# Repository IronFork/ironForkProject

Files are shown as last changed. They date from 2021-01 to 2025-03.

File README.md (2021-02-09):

# ironForkProject
 robotic arm helping people with disabilities to eat
 
 https://ironfork.fr

READ ME

I - INTRODUCTION

  a) Présentation
  
  b) Objectifs du projet
  
II - MONTER LE ROBOT

  a) Imprimer les pièces en 3D
  
  b) Se procurer les moteurs
  
  c) Se procurer les composants annexes 
  
III - FAIRE FONCTIONNER LE ROBOT

IV - EXPLICATION DU CODE SOURCE

  a) La partie mécanique 
  
  b) La partie programmation
  
V - PISTES D'AMÉLIORATION

I - INTRODUCTION 

a) Présentation : 
Projet mené par un groupe de 12 étudiants en partenariat avec l'IEM "Christian Dabbadie" dans le cadre de leurs études à Centrale Lille. 

b) Objectifs du projet : 
Concevoir un bras robotique permettant aux personnes en situation de handicap d'avoir une plus grande autonomie lors de leurs repas. 
Projet en open source avec une licence GPL. 
L'un des objectifs du projet est de rendre le bras imprimable en 3D facilement dans un fablab.

I - MONTER LE ROBOT 

Vous aurez besoin d'une imprimante 3D et de ... bobines de PLA. Le reste des composants à commander est indiqué dans les étapes suivantes. Le budget estimé est de 500€ environs. 

a) Imprimer les pièces en 3D : 
Ouvrir le dossier fichiers_stl. Ce dossier contient les fichiers STL de chaque pièce du robot, organisées en sous-ensembles. Un sous-dossier nommé "assemblages" contient les fichiers STL des différents sous-ensembles, et de l'assemblage complet. 

Liste des pièces à imprimer en 3D : 

Pour le socle : 
  - 3 sous-socles différents (c'est le plancher du robot, les 3 sous-socles sont sur le même ficher STL)
  - 1 bol
  - 1 socle (en forme de petite tablette)
  - 1 adaptateur socle-moteur (permet de fixer le moteur sous le socle)
  - 1 poulie socle (poulie fixée sur l'axe moteur)
  
Pour la Tourelle : 
  - 1 Tourelle (placée en liaison pivot avec le socle, elle soutient le bras)
  - 1 poulie tourelle ( poulie fixée dans l'axe de la tourelle et reliée à la poulie socle par une courroie)
  - 2 adaptateurs tourelle-moteurs (permettent de fixer 2 moteurs sur la tourelle)
  
Pour le bras : 
  - 1 bras Tourelle (c'est le bras relié à la tourelle en pivot)
  - 1 adaptateur bras-moteur (permet de fixer le moteur sur le bras)
  
Pour l'avant-bras : 
  - 1 avant-bras (ressemble au bras-tourelle mais est légèrement différent)
  - 1 adaptateur avant-bras-moteur (permet de fixer le moteur)
  
Pour la pince : 
  - 1 pince 

Pour l'assemblage, référez-vous aux fichiers STL représentant les sous-ensembles du robot. 

b) Se procurer les moteurs : 
Vous aurez besoin de cinq moteurs dynamixel XL430-W250-T.
documentation technique sur github : https://github.com/ROBOTIS-GIT/emanual/blob/master/docs/en/dxl/x/xl430-w250.md

c) Se procurer les composants annexes : 
voir notice. (visserie, fils électriques, rasberry pi, carte de programmation, etc... )

d) Assembler le robot : 
Vous devez vous référer au dossier fichiers_stl pour voir le rôle de chaque composant au sein de l'assemblage complet. 
Référez-vous également au schéma électrique pour les différents branchements. 
Référez-vous à la notice pour vous aider

L'assemblage du robot est maintenant terminé. 

II - FAIRE FONCTIONNER LE ROBOT  

Version 1 du robot 

La trajectoire est programmée par l'ensemble des fichiers matlab 
puis est lue par le programme IronFork.c

Version 2 du robot 

Compiler IronForkV3.c et l'executer. Le robot pourra apprendre sa trajectoire pendant une phase de teaching et ensuite la répeter. 

III - EXPLICATION DU CODE SOURCE 

a) La partie mécanique

Le schéma cinématique : 
Nous avons choisi un nombre de 5 pièces d'un point de vue cinématique. Elles sont reliées en série au bâti par cinq liaisons pivot. Une pivot verticale lie le BATI avec la TOURELLE, une pivot horizontale lie la TOURELLE au BRAS, une pivot horizontale lie le BRAS à l'AVANT-BRAS, et une liaison pivot horizontale lie l'AVANT-BRAS à la PINCE. 
Ce choix de 4 pièces et de cinq liaisons pivot nous permet de positionner la PINCE à n'importe quel endroit dans l'espace, et de réaliser un maximum de mouvements en gardant la PINCE à l'horizontal (ce qui permet de déplacer une cuillère sans renverser son contenu). Ce choix de cinématique permet des mouvements fluides et précis. Référez-vous au fichier STL de l'assemblage complet pour vous représenter l'architecture du robot. 

La tourelle : 
La tourelle est au bâti par une liason pivot verticale. Cette liaison permet au robot de tourner sur lui même et de déplacer la cuillère de manière grossière latéralement de gauche à droite. 
Cette liasion qui est la première est la seule à supporter toute la structure du robot, et subit donc beaucoup d'efforts. Il y a également beaucoup de forttements, de par l'appui de la tourelle sur le bâti. Nous avons choisi d'utiliser un coussinet à collerette entre le bati et la tourelle pour minimiser les frottements. La liasion est motorisée par un servomoteur Dynamixel positionné à quelques centimètres de la liaison, et relié par une liaison poulie-couroie. Cela permet de résoudre le problème de coaxialité du moteur avec la liasion, et d'écentuels efforts supportés par l'axe du moteur.

La tourelle et le bras : 
La tourelle et le bras sont reliés par une liaison pivot horizontale. Cette liaison contribue grandement au mouvement d'avant en arrière de la cuillère. 
Encore une fois, cette liasion supporte une bonne partie de la structure du robot, surtout quand celui-ci est étendu. Dans ce cas là, le couple dans l'axe de la liaison est particulièrement élevé. C'est pourquoi nous avons choisi de placer non pas un, mais deux servomoteurs Dynamixel en parallèle de manière à pouvoir axionner cette liasion avec une puissance suffisante. Deux adaptateurs sont vissés au bâti avec des vis à bois permettent de fixer les servomoteurs. 

Le bras et l'avant-bras : 
Le bras est relié à l'avant-bras par une liasion pivot motorisée par un servomoteur Dynamixel. Cette laison contribue grandement au mouvement vertical de bas en haut de la cuillère. Un adaptateur vissé au bras par des vis à bois permet de fixer le moteur. 

L'avant-bras et la pince : 
L'avant-bras et la pince sont reliés entre eux par une liaison pivot motorisée par un servomoteur Dynamixel. Cette liaison permet d'effectuer un mouvement vertical de précison, à la manière d'un poignet. Un adaptateur vissé à l'avant-bras permet de fixer le moteur. 

La pince : 
La pince présente une fente ainsi qu'un trou. Ce trou permet d'y placer un insert de filletage, et la fente permet d'y glisser un manche de cuillère. Ainsi, avec une vis de pression, la cuillère peut être bloquée dans la fente. L'avantage de ce système est qu'il permet l'utilisation d'une cuillère quelconque. 

Le bol : 
Un bol imprimé en 3D est fixé sur le support. ce bol a une forme particulière qui permet à la nourriture d'être centrée dans la zone de pelletage. De plus, le rebord avancé peu haut et le rebord éloigné élevé permettent une introduction de la cuillère aisée, et un raclage facilité. L'avantage de ce système est qu'il permet de n'avoir qu'un seul et unique geste de peletage pour le robot. L'inconvénient est le côté sanitaire : il faut imprimer le bol en PET, et les stries de l'impression 3D peuvent occasionner des copeaux de plastiques dans la nourriture lors du raclage. 

b) La partie programmation

cf commentaires

IV - PISTES D'AMELIORATION

- sécurité, détection d'erreur informatique
- tests en conditions réeelles (personne en situation de handicap)
- améliorer le système de fixation de la cuillère 
- réduire le volume
- trouver des composants moins cher
- reconnaissance faciale
- ...

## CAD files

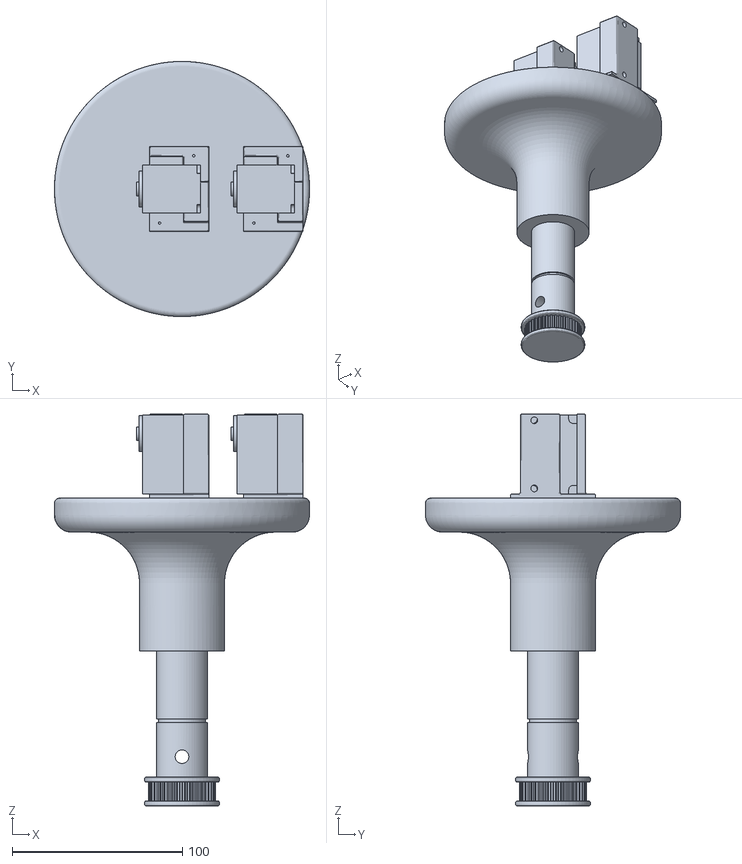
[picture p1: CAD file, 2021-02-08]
Ancien projet/fichiers_STL/assemblages/Tourelle.stl
150.0 x 150.0 x 230.4

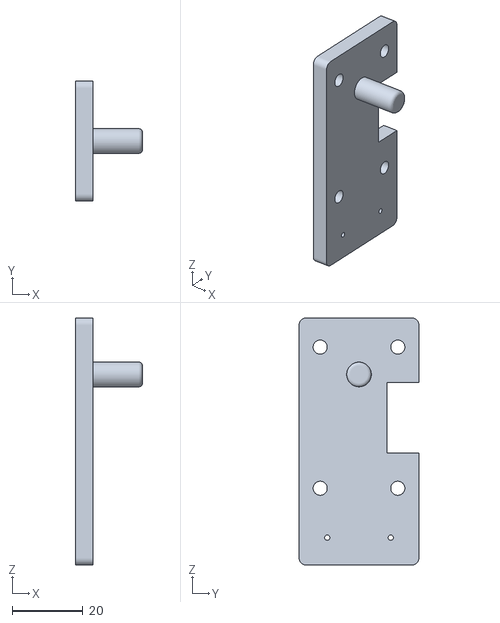
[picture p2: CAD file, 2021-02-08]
Ancien projet/fichiers_STL/avant-bras/Adaptateur Bras-Moteur.stl
19.0 x 34.0 x 70.0

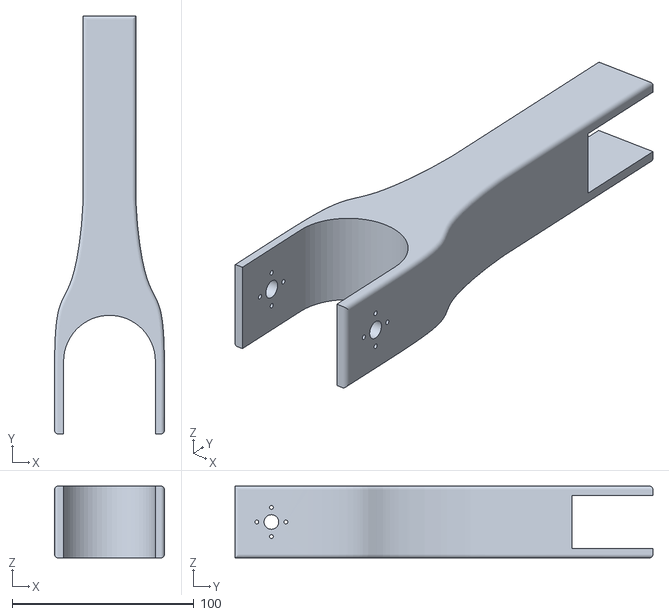
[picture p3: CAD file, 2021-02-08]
Ancien projet/fichiers_STL/bras/Bras Tourelle.stl
60.5 x 229.7 x 39.5

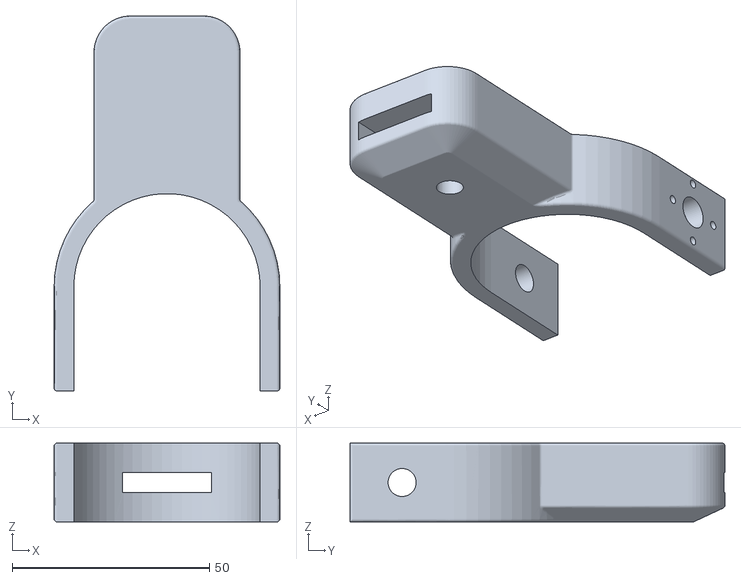
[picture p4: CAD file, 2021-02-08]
Ancien projet/fichiers_STL/pince/Pince-2.stl
57.2 x 95.0 x 20.0

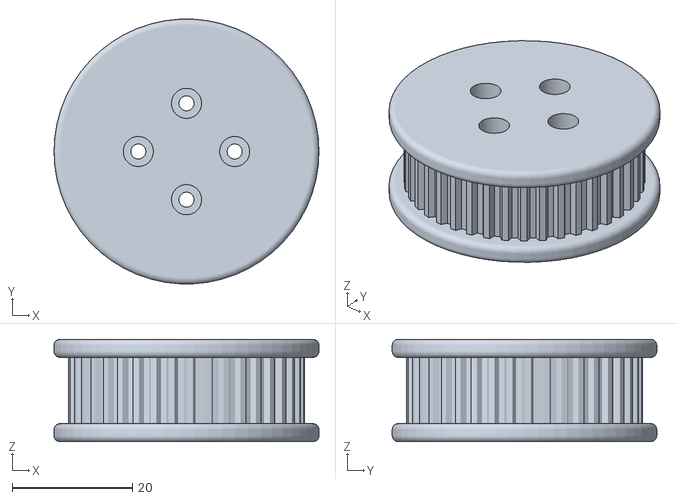
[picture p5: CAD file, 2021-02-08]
Ancien projet/fichiers_STL/socle/Poulie Socle.stl
44.0 x 43.9 x 17.0

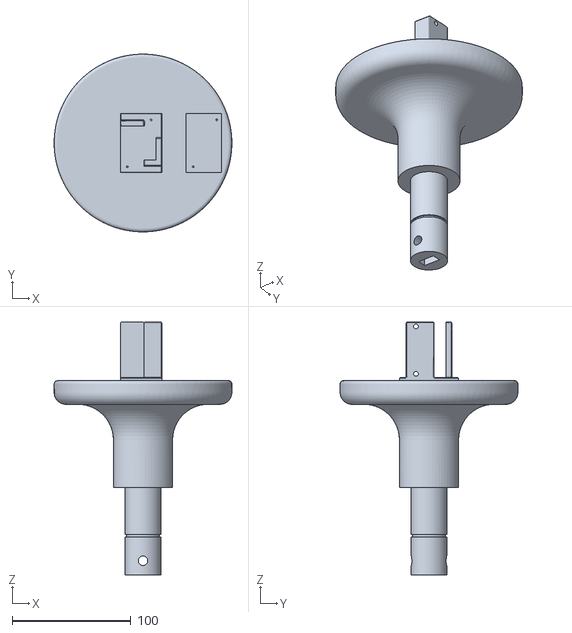
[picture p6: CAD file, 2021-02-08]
Ancien projet/fichiers_STL/tourelle/Tourelle.stl
150.0 x 150.0 x 213.4

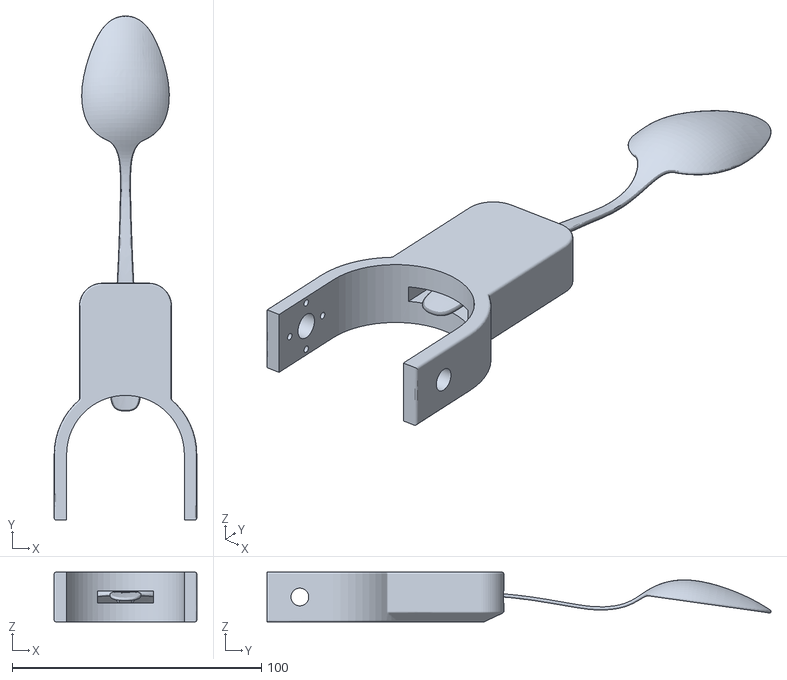
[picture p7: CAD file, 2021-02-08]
Ancien projet/fichiers_STL/assemblages/Pince-2.stl
57.2 x 202.2 x 20.0

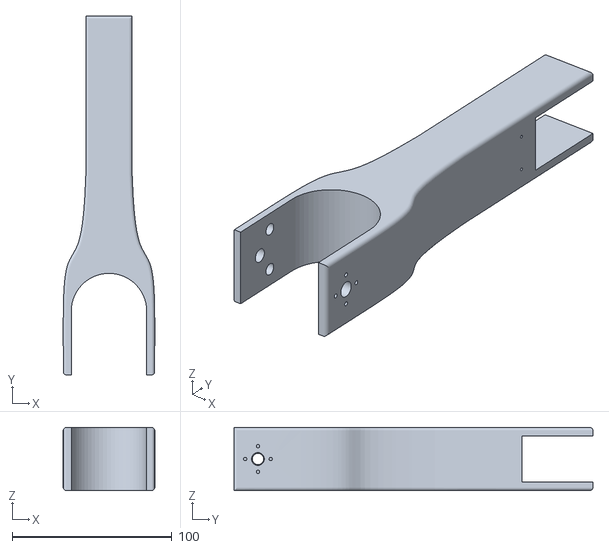
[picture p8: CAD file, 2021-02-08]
Ancien projet/fichiers_STL/avant-bras/Avant-Bras.stl
57.3 x 224.7 x 39.5

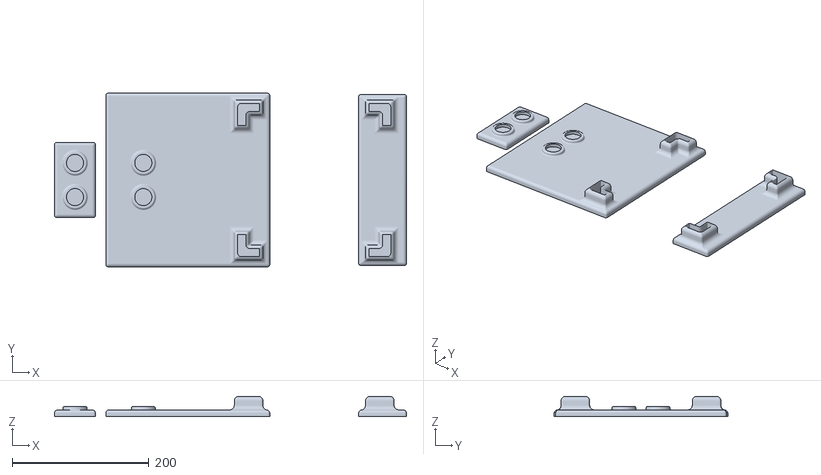
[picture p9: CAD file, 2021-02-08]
Ancien projet/fichiers_STL/socle/Sous-Socles.stl
515.0 x 254.0 x 30.0

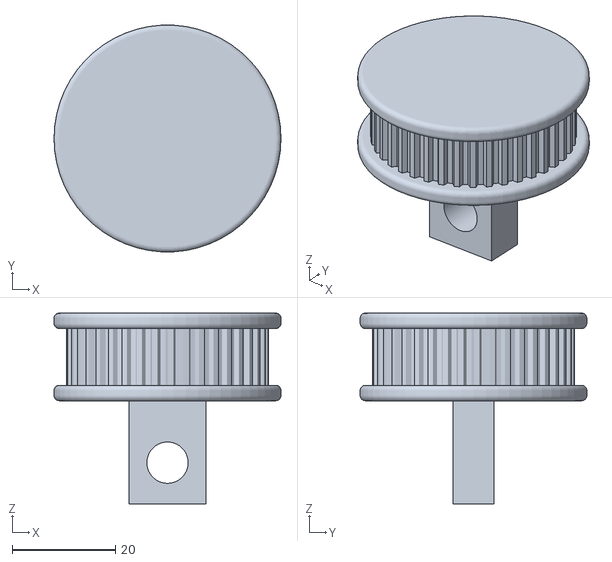
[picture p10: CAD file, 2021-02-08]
Ancien projet/fichiers_STL/tourelle/Poulie Tourelle.stl
44.0 x 43.9 x 37.0

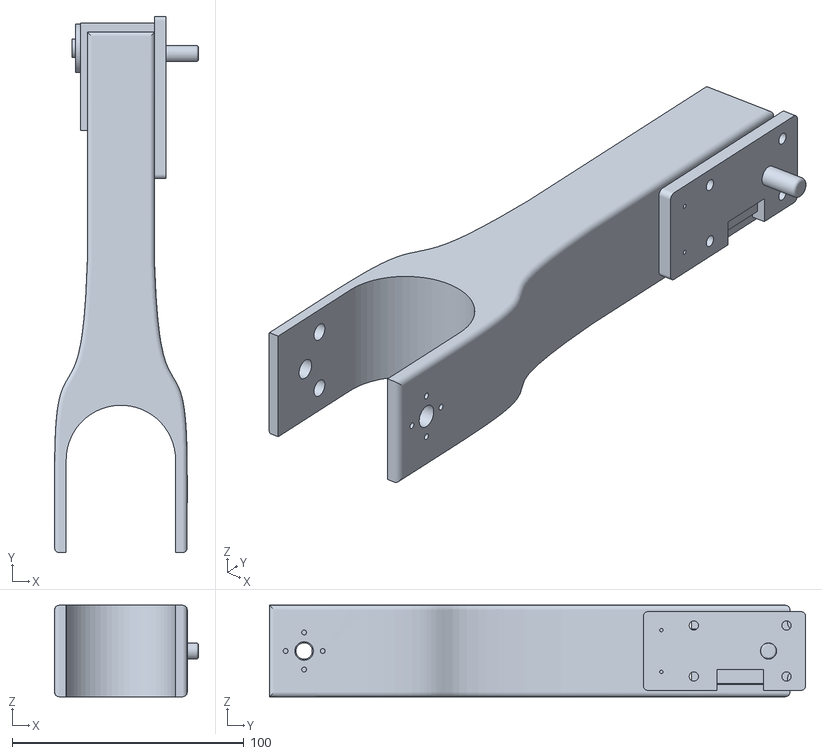
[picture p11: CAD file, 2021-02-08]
Ancien projet/fichiers_STL/assemblages/Avant-Bras.stl
62.2 x 231.4 x 39.5

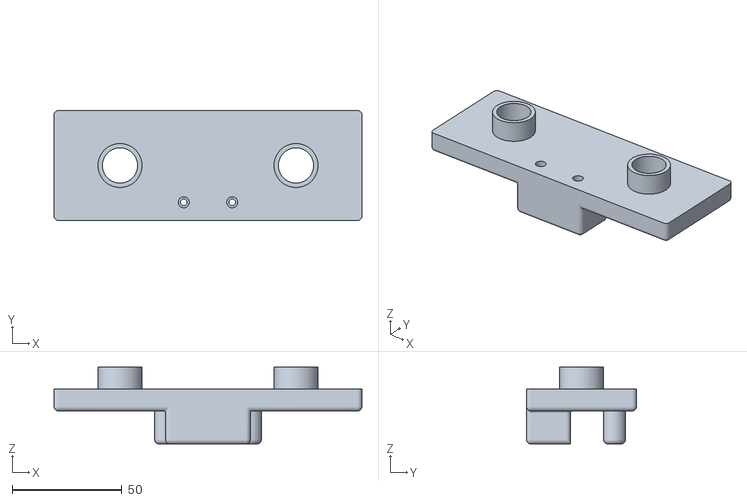
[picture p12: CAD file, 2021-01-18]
Ancien projet/fichiers_STL/socle/Adaptateur Socle-Moteur-1.stl
140.0 x 50.0 x 35.0

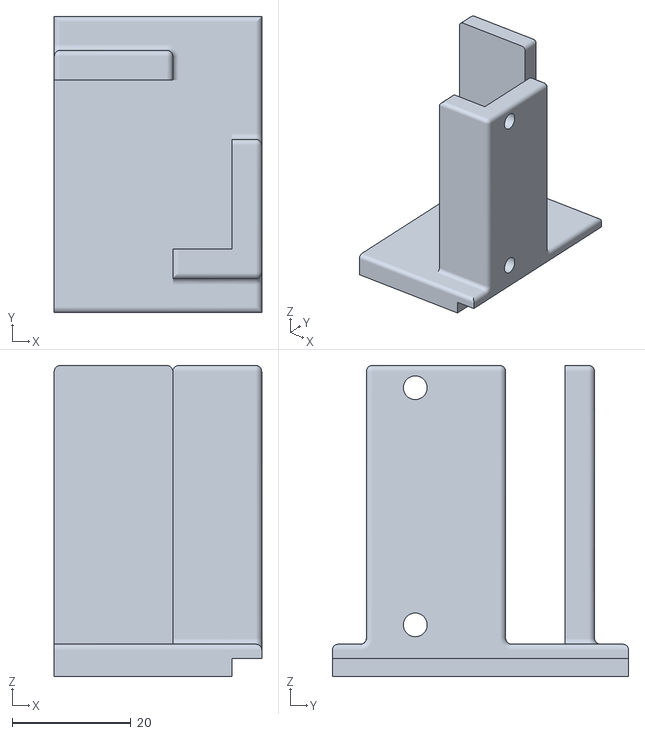
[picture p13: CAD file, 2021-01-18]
Ancien projet/fichiers_STL/tourelle/Adaptateur Tourelle Moteur (1).stl
35.0 x 50.0 x 52.4

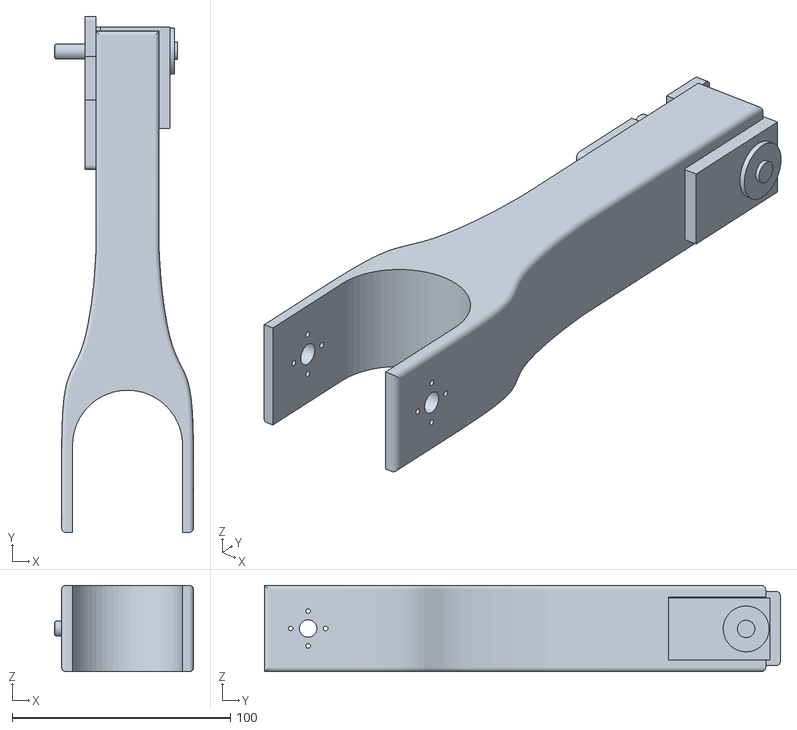
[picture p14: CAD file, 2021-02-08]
Ancien projet/fichiers_STL/assemblages/Bras.stl
63.8 x 236.4 x 39.5

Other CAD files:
Ancien projet/fichiers_STL/socle/Socle.stl
Ancien projet/fichiers_STL/socle/Bol.stl

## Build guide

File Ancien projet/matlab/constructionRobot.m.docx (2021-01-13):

%% création du robot

IronFork = rigidBodyTree;

% création des parties du robot

tourelle = rigidBody('tourelle');

bras = rigidBody('bras');

avantBras = rigidBody('avantBras');

pince = rigidBody('pince');

% création des joint entre parties

jnt1 = rigidBodyJoint('jnt1','revolute');

jnt2 = rigidBodyJoint('jnt2','revolute');

jnt3 = rigidBodyJoint('jnt3','revolute');

jnt4 = rigidBodyJoint('jnt4','revolute');

%% Paramètrage des joints

% Liaison bati-tourelle

jnt1.HomePosition = alpha1; %position initiale du moteur

%Placement de la liaison.

tform1 = trvec2tform([0, 0, 0]);

setFixedTransform(jnt1,tform1); %applique la transformation

tourelle.Joint = jnt1; %liaison du joint au corps

% Liaison tourelle-bras

jnt2.HomePosition = alpha2; %position initiale du moteur

tform2 = trvec2tform([0, 0, AB])*eul2tform([0, -pi/2, 0]);

setFixedTransform(jnt2,tform2);

bras.Joint = jnt2;

% Liaison bras-avantBras

jnt3.HomePosition = alpha3; %position initiale du moteur

tform3 = trvec2tform([BC, 0, 0]);

setFixedTransform(jnt3,tform3);

avantBras.Joint = jnt3;

% Liaison avantBras-pince

jnt4.HomePosition = alpha4; %position initiale du moteur

tform4 = trvec2tform([CD, 0, 0]);

setFixedTransform(jnt4,tform4);

pince.Joint = jnt4;

%% Mise en place robot

addBody(IronFork,tourelle,'base');

addBody(IronFork,bras,'tourelle');

addBody(IronFork,avantBras,'bras');

addBody(IronFork,pince,'avantBras');

%% Ajout end effector

cuillereBout = rigidBody('cuillereBout');

tform5 = trvec2tform([DE, 0, 0])*eul2tform([0, 0, pi/2]); % User defined

setFixedTransform(cuillereBout.Joint,tform5);

addBody(IronFork,cuillereBout,'pince');

%% Visualisation

q0=homeConfiguration(IronFork);

showdetails(IronFork);

show(IronFork,q0);

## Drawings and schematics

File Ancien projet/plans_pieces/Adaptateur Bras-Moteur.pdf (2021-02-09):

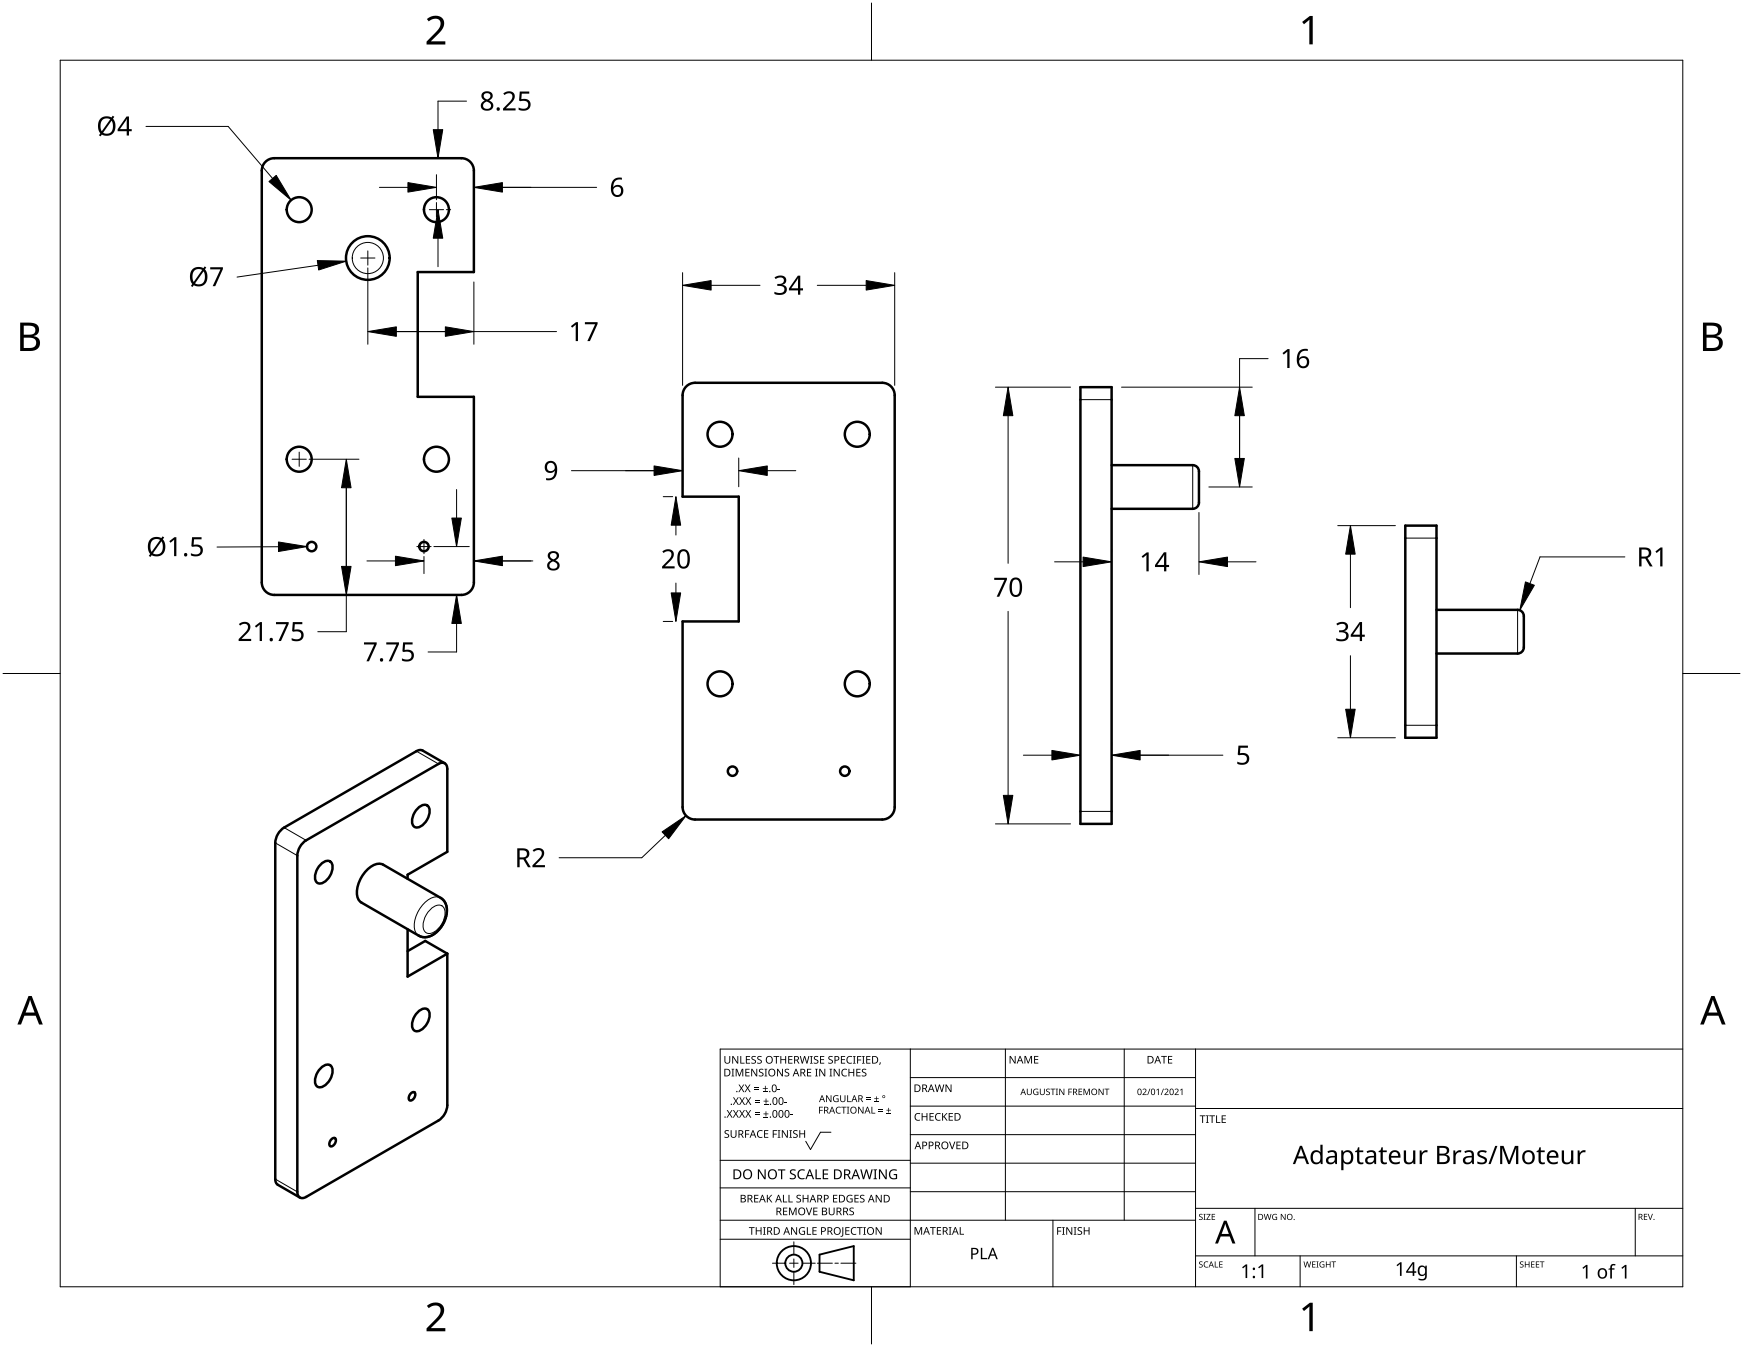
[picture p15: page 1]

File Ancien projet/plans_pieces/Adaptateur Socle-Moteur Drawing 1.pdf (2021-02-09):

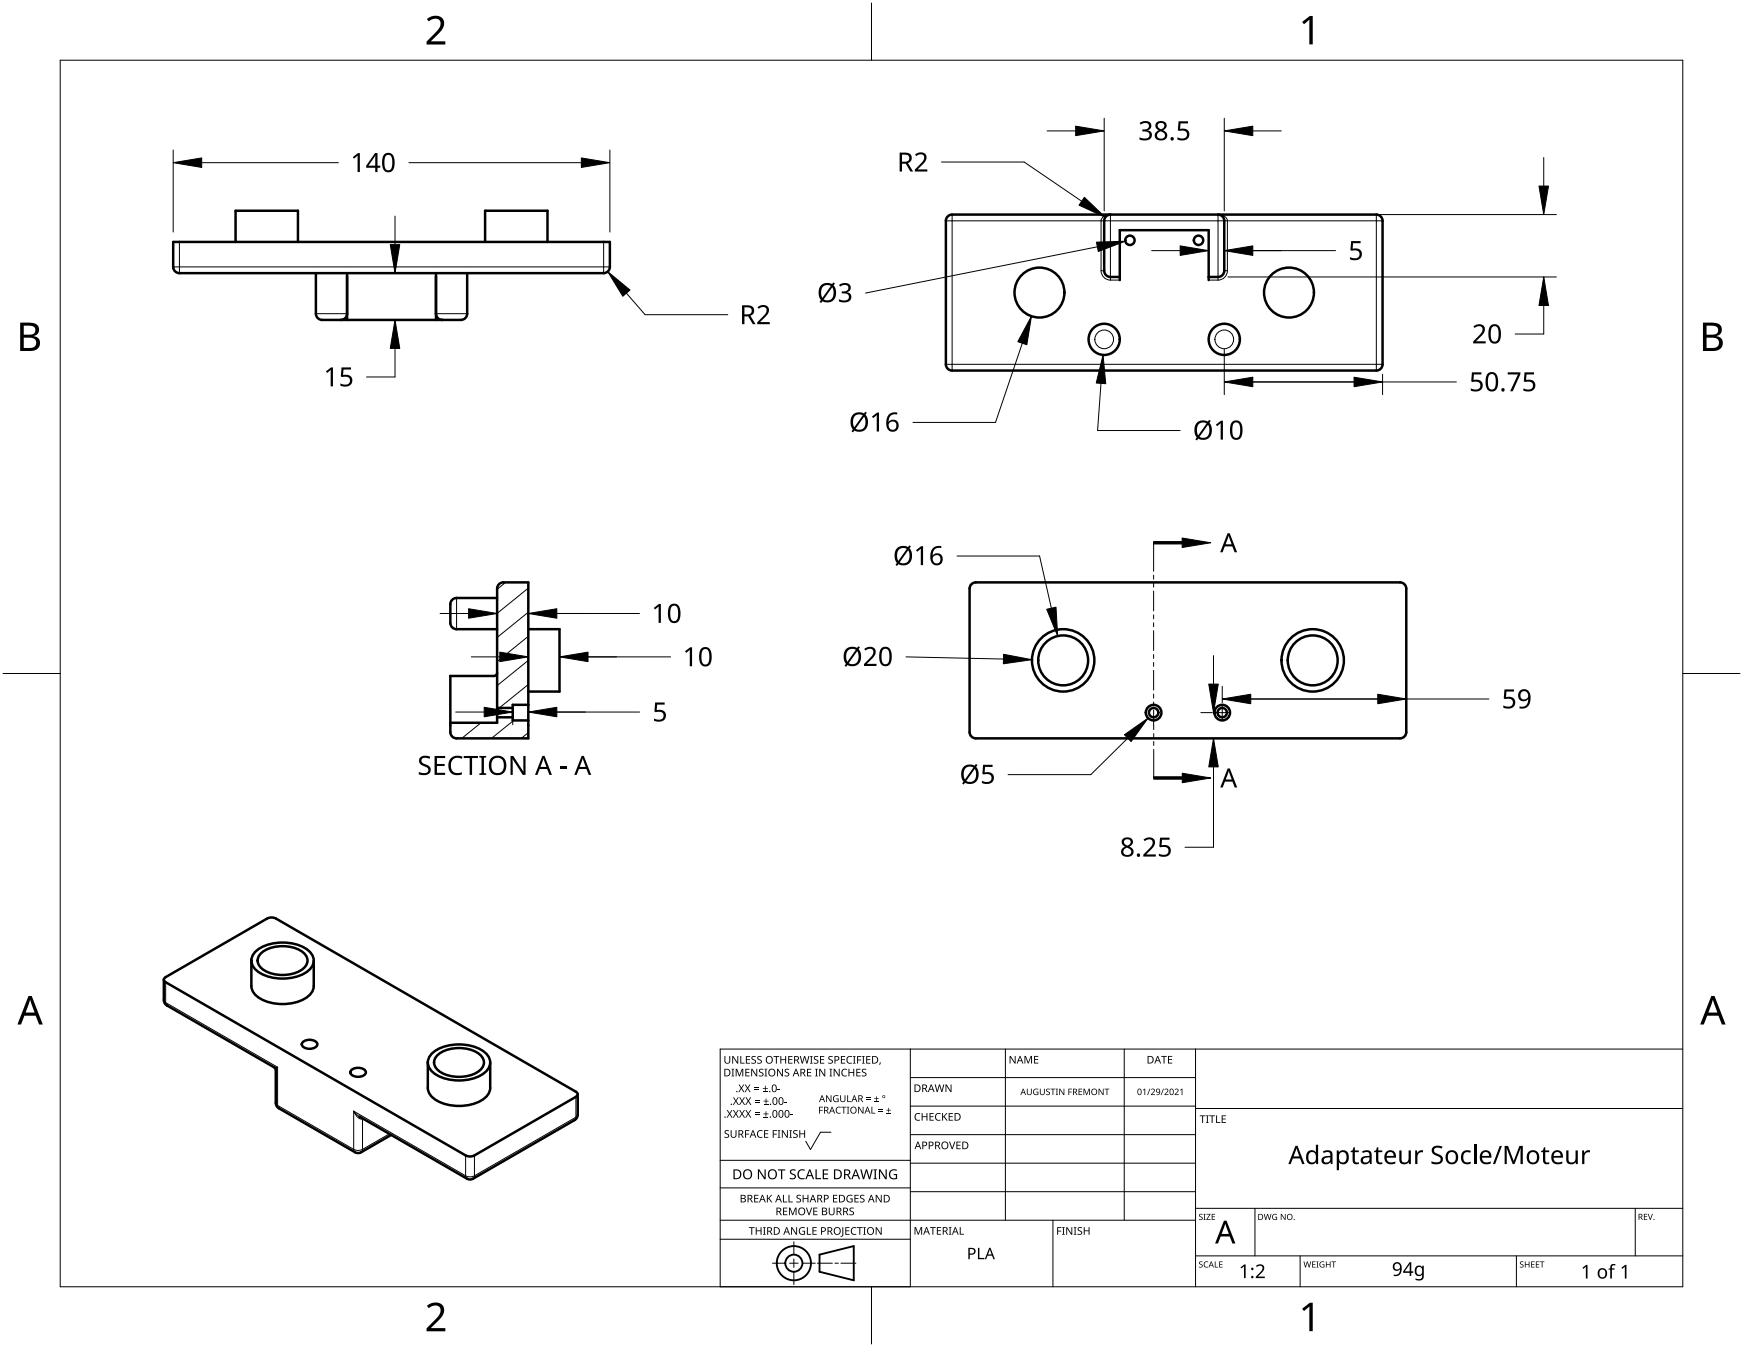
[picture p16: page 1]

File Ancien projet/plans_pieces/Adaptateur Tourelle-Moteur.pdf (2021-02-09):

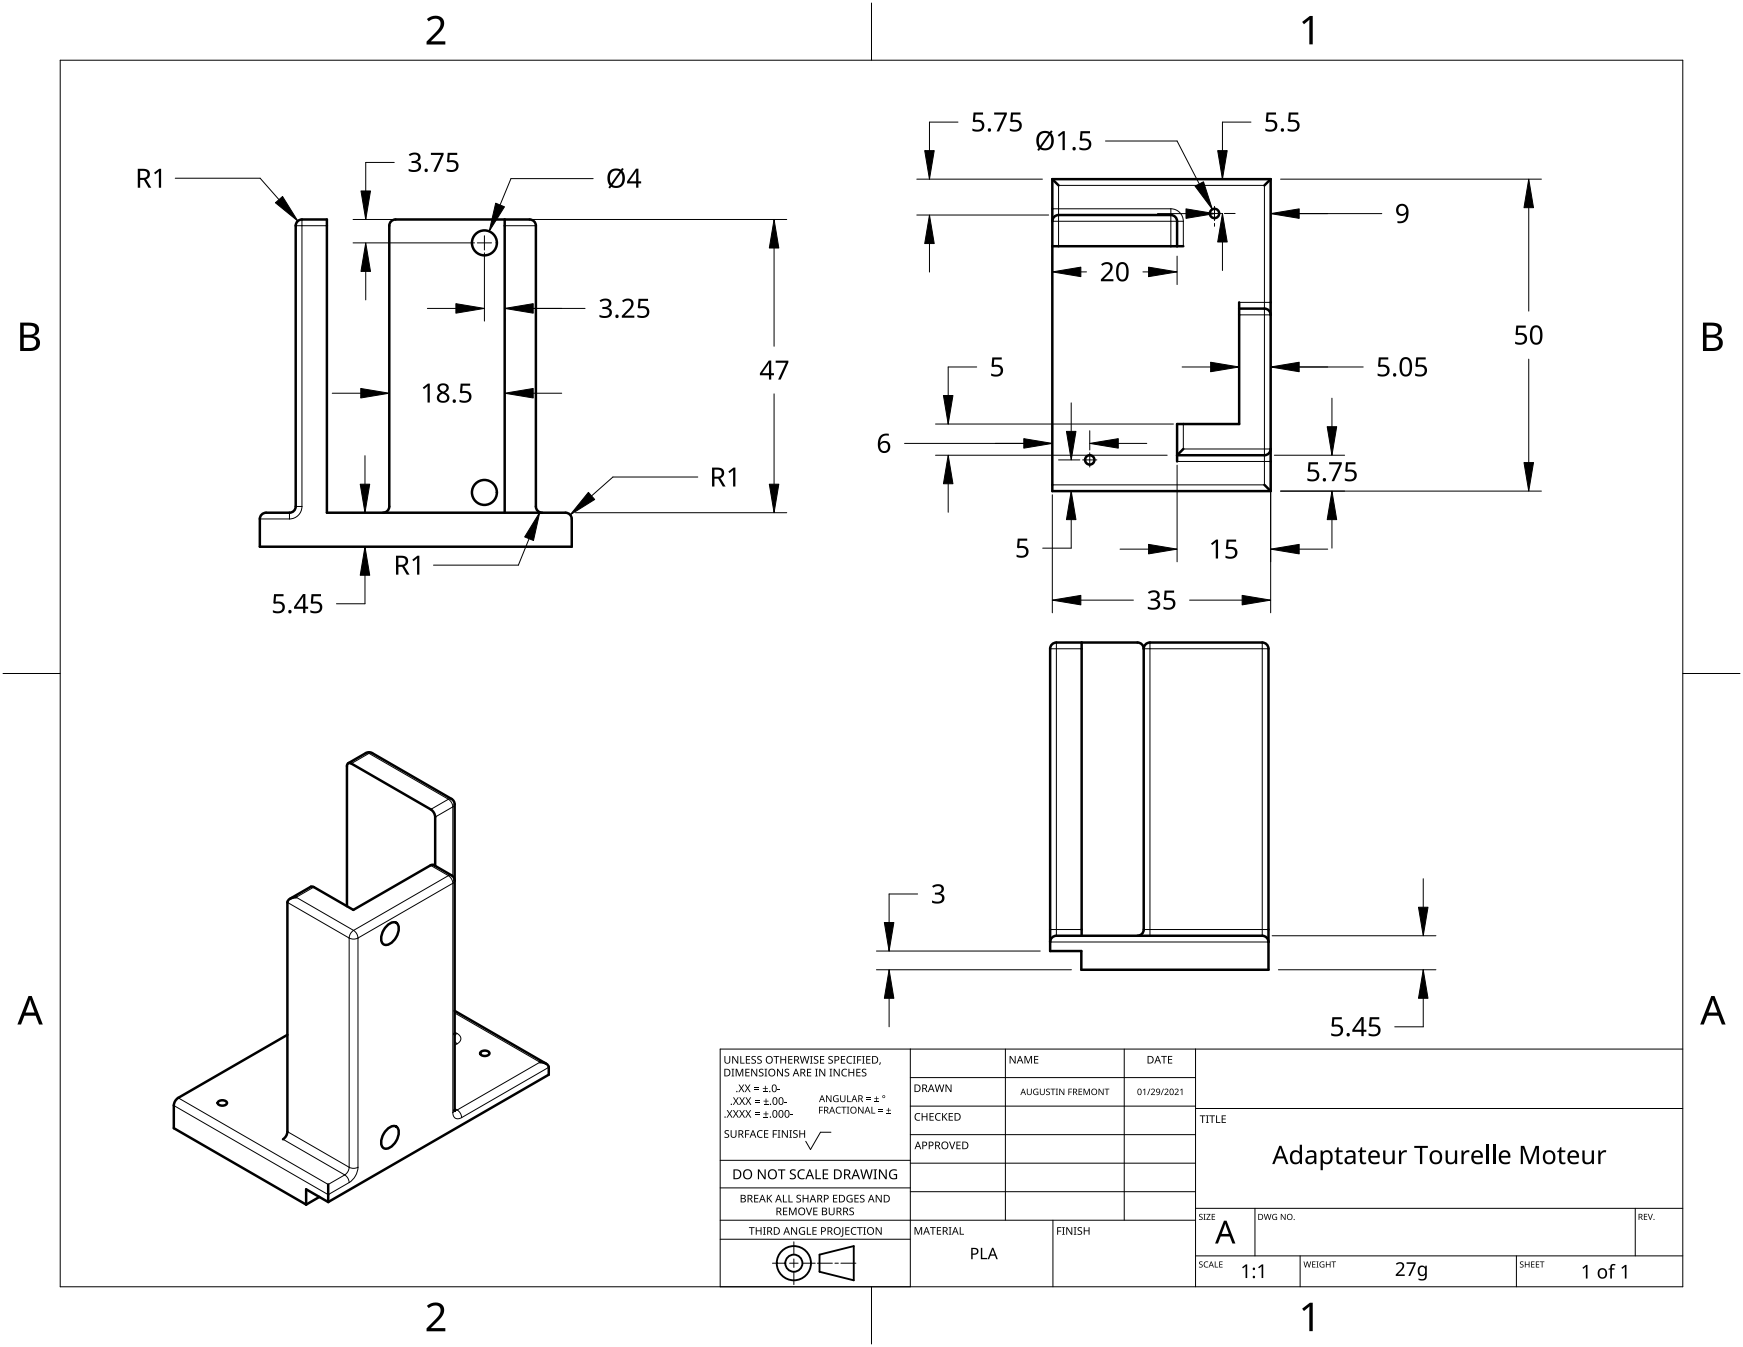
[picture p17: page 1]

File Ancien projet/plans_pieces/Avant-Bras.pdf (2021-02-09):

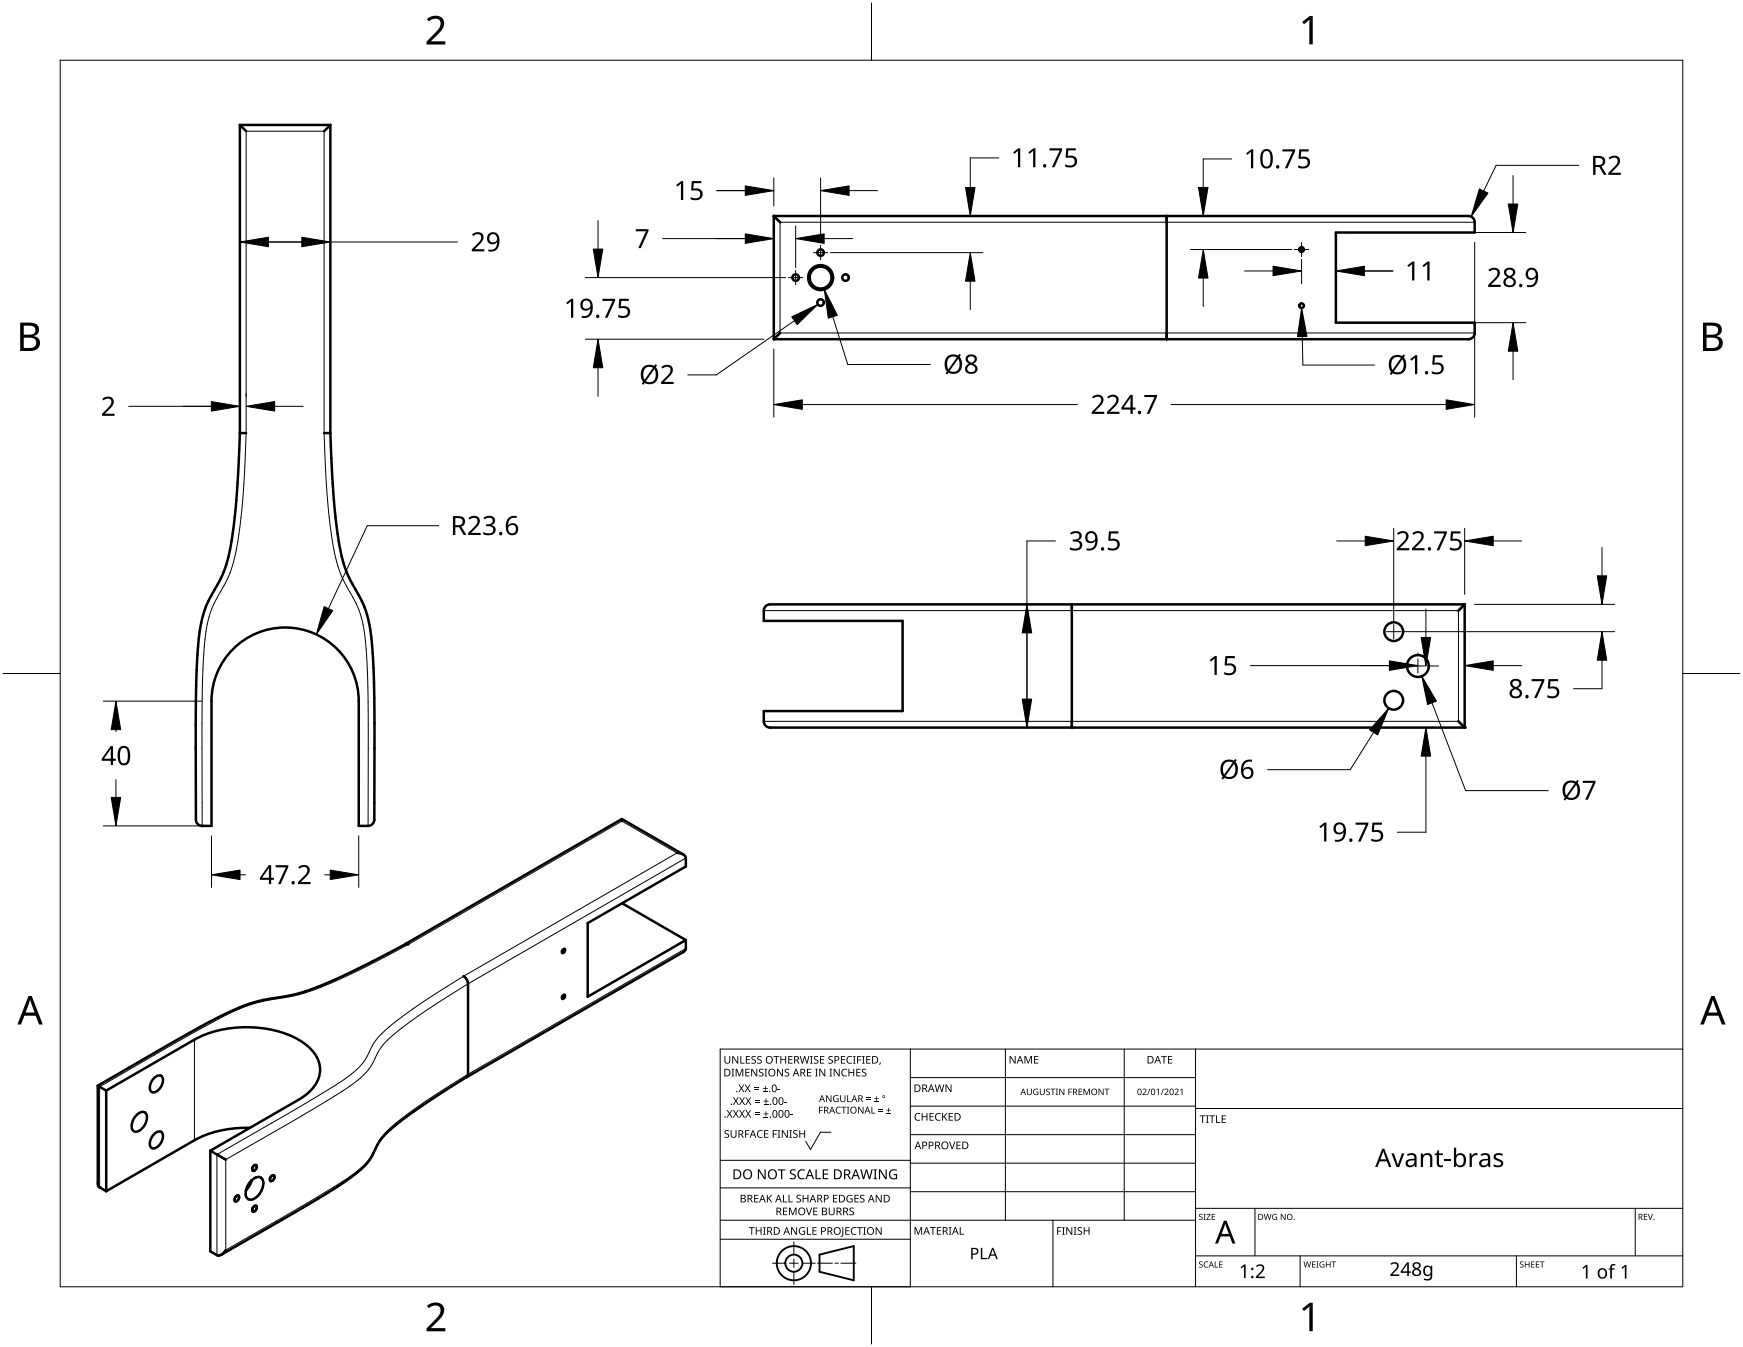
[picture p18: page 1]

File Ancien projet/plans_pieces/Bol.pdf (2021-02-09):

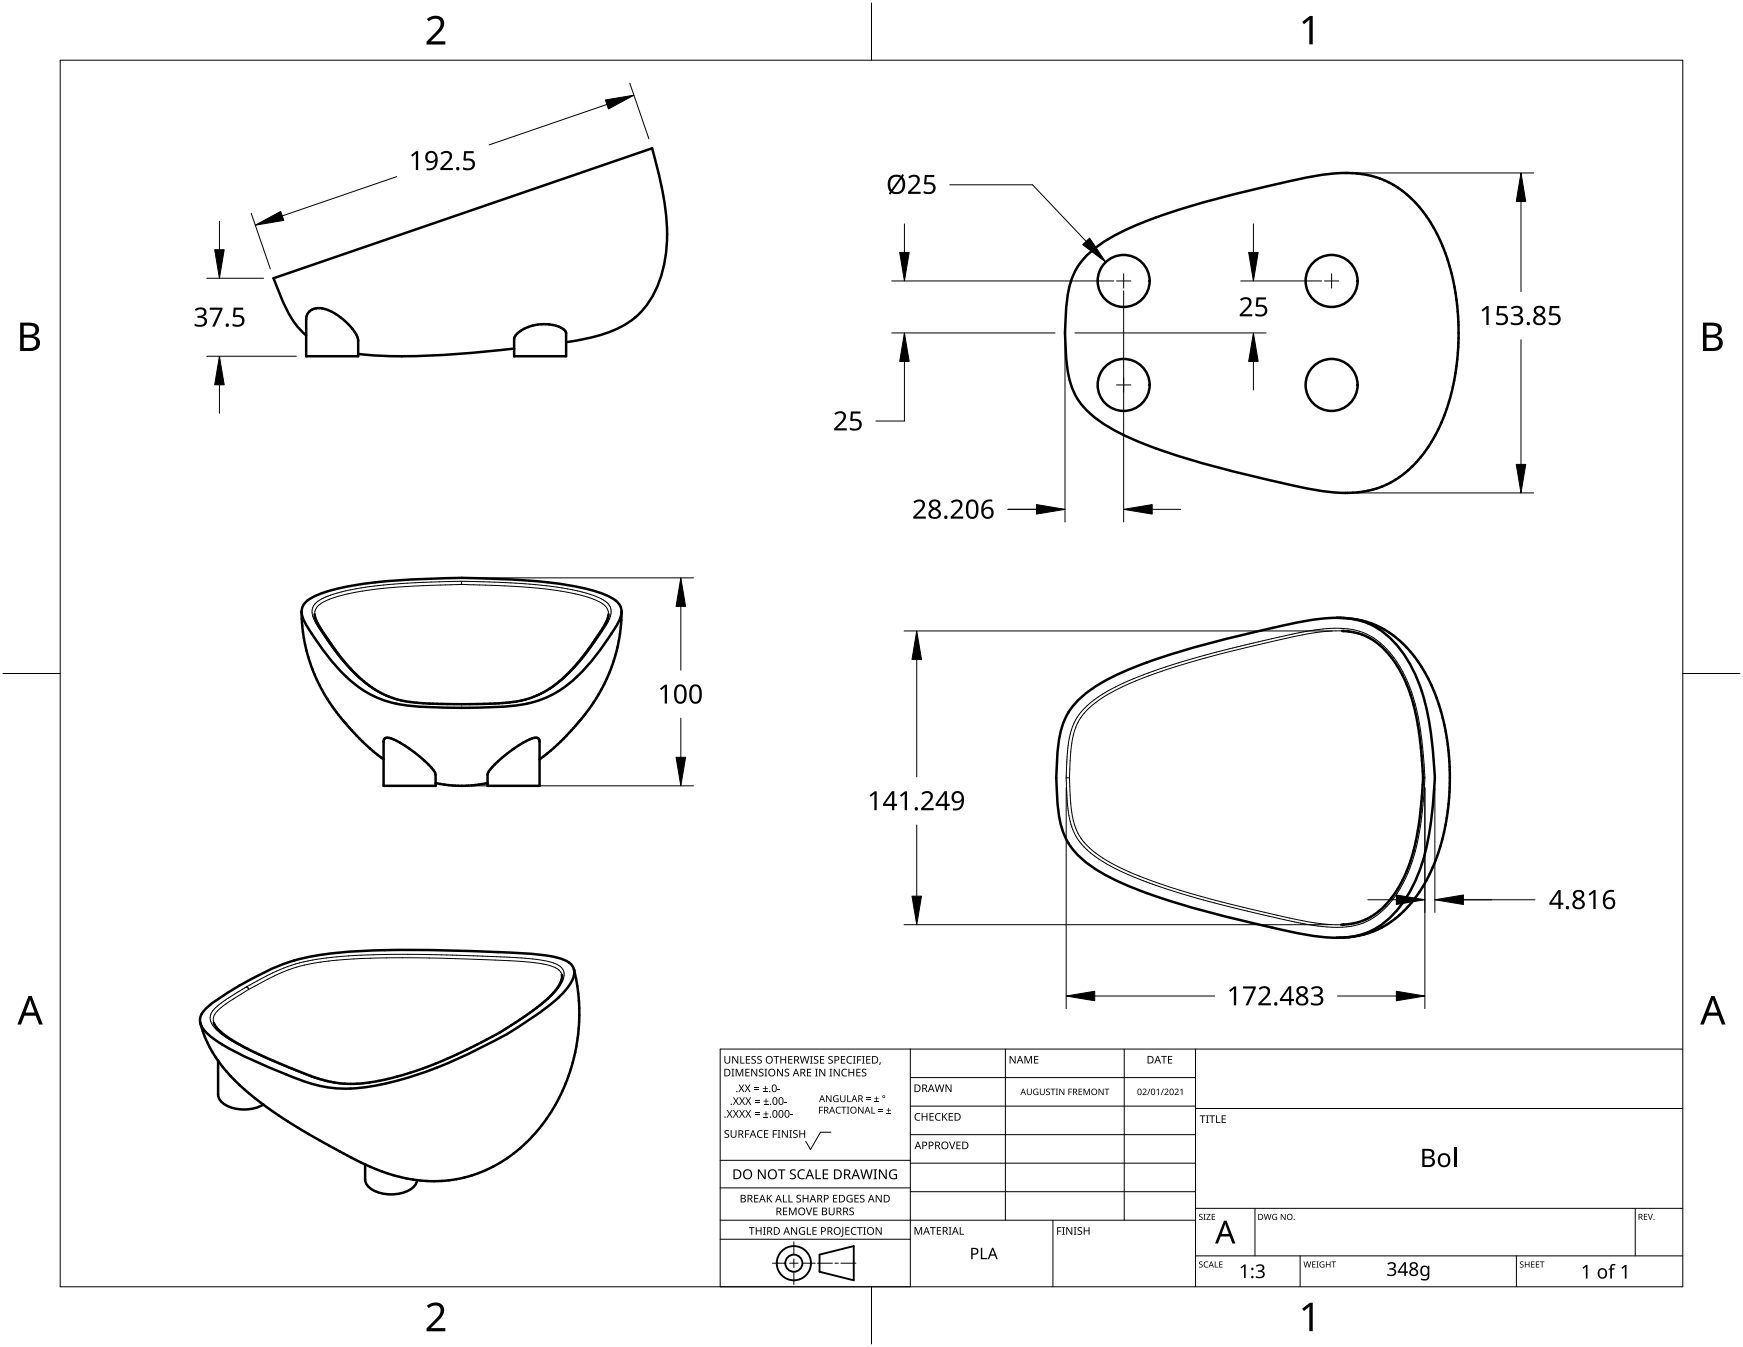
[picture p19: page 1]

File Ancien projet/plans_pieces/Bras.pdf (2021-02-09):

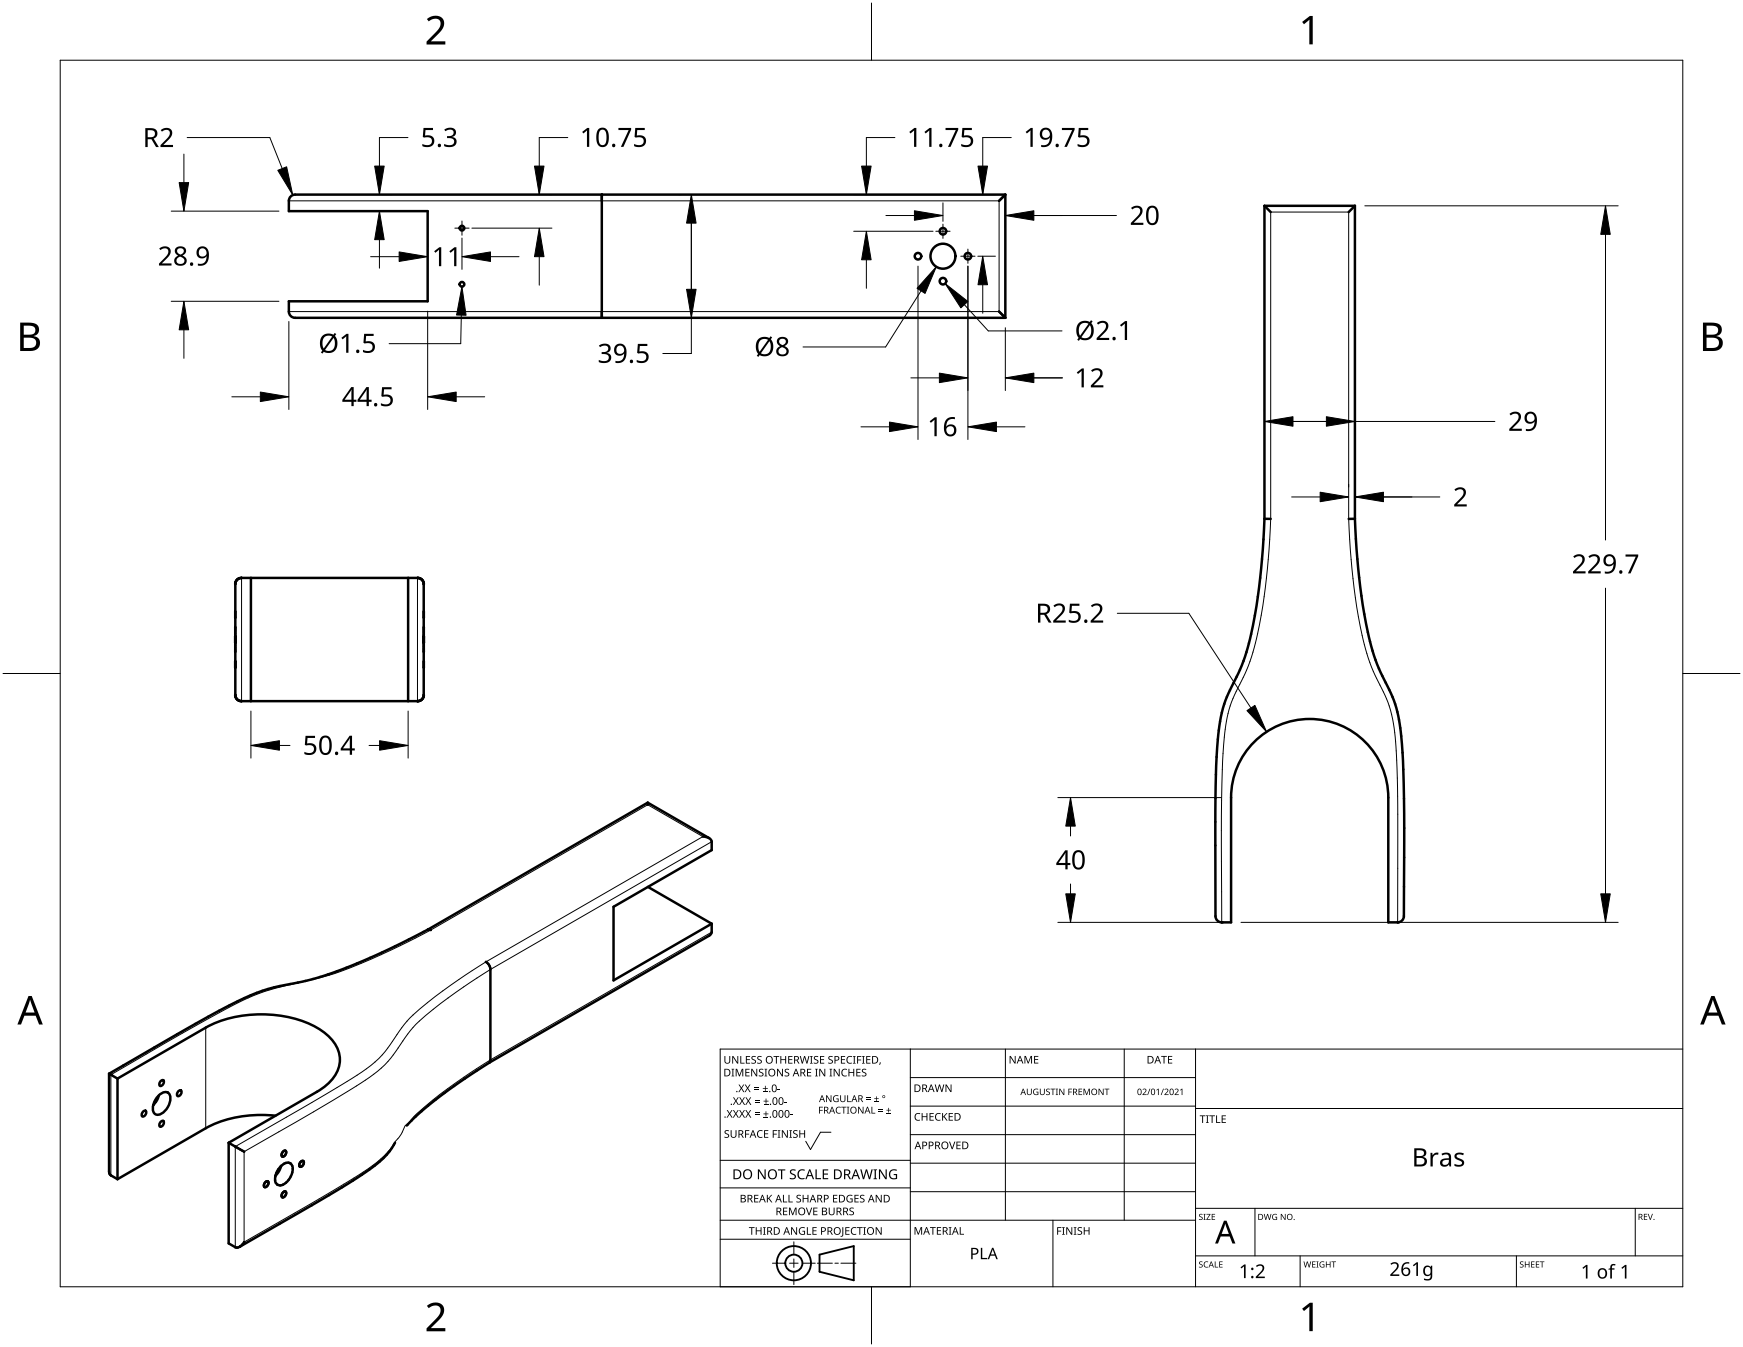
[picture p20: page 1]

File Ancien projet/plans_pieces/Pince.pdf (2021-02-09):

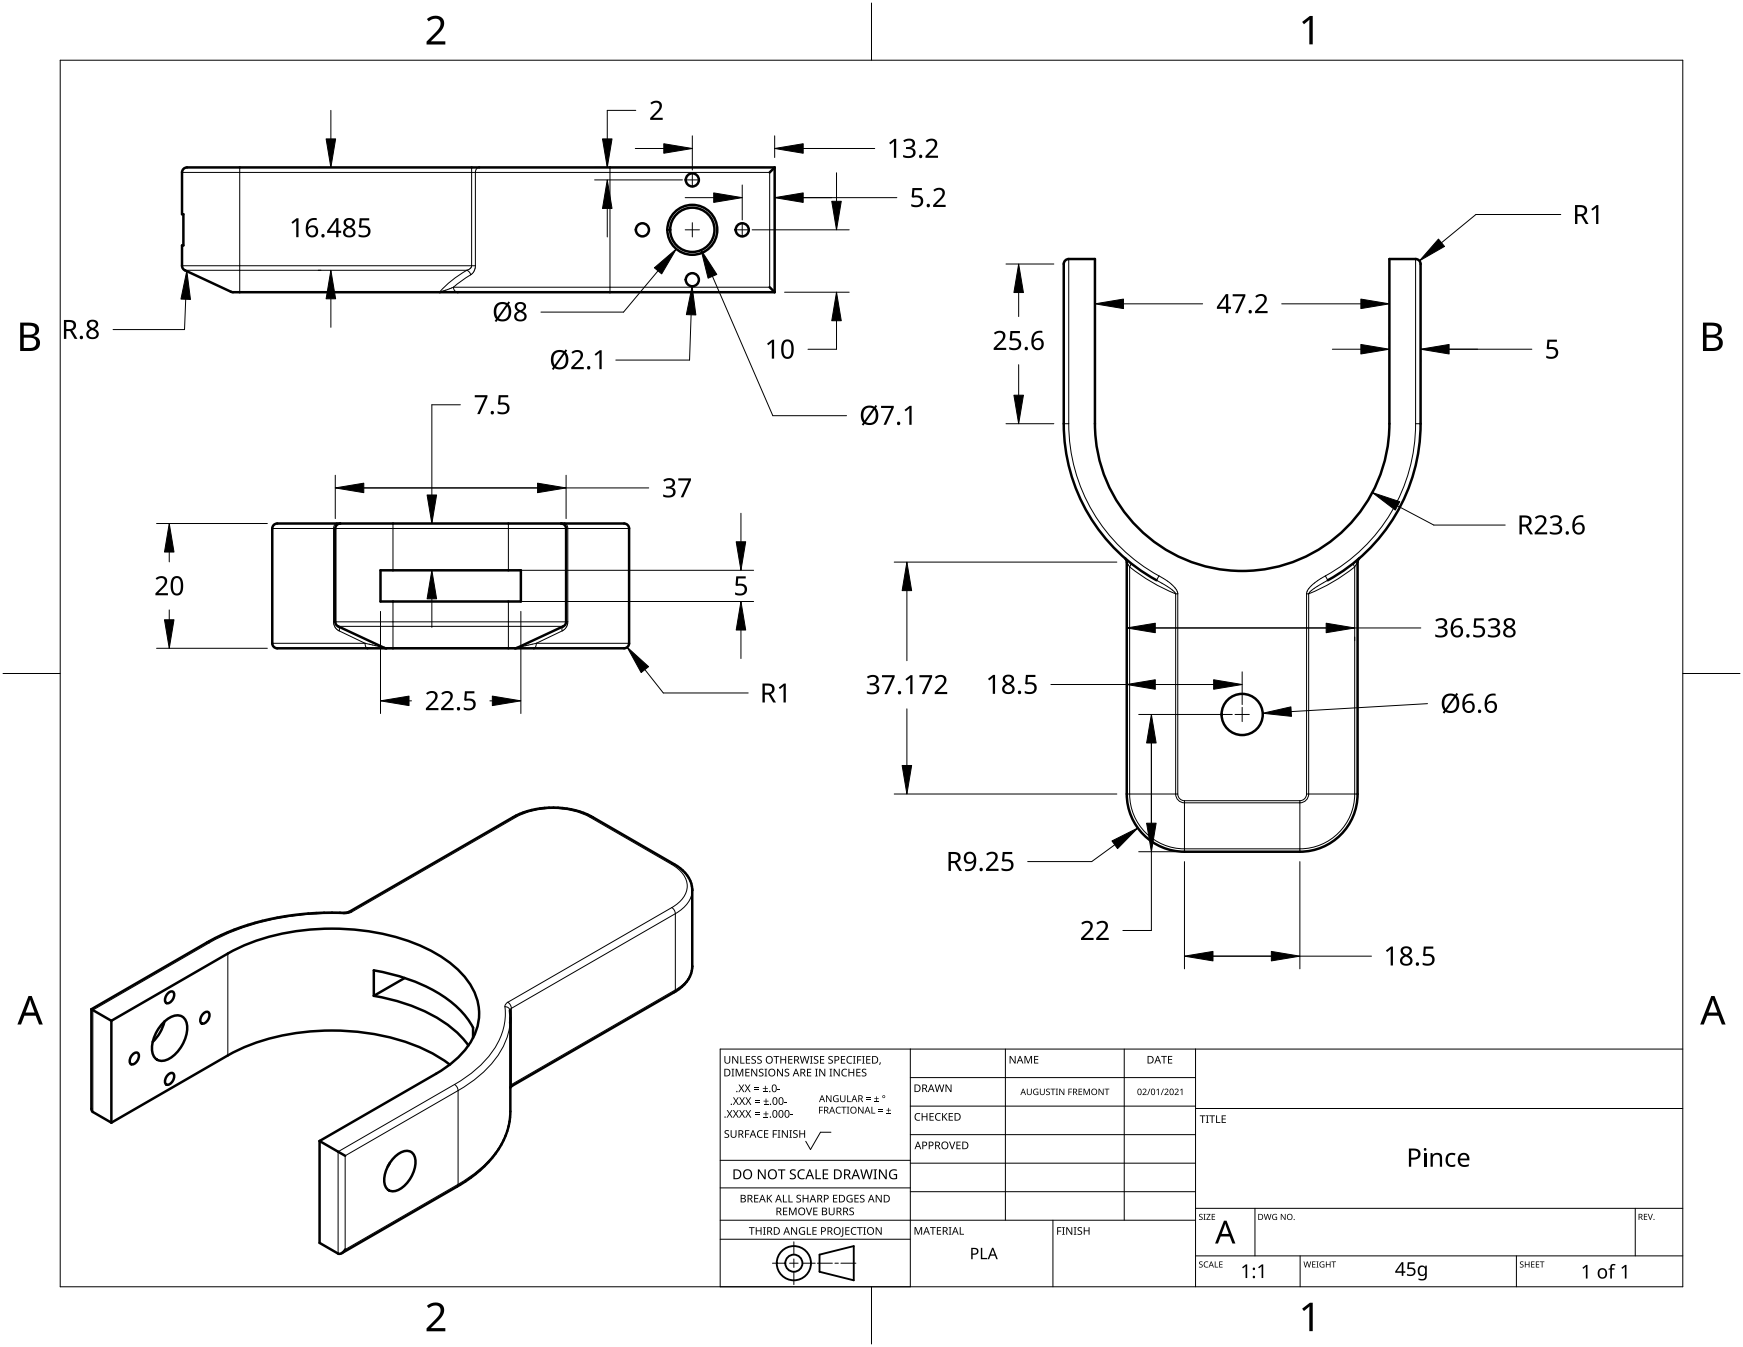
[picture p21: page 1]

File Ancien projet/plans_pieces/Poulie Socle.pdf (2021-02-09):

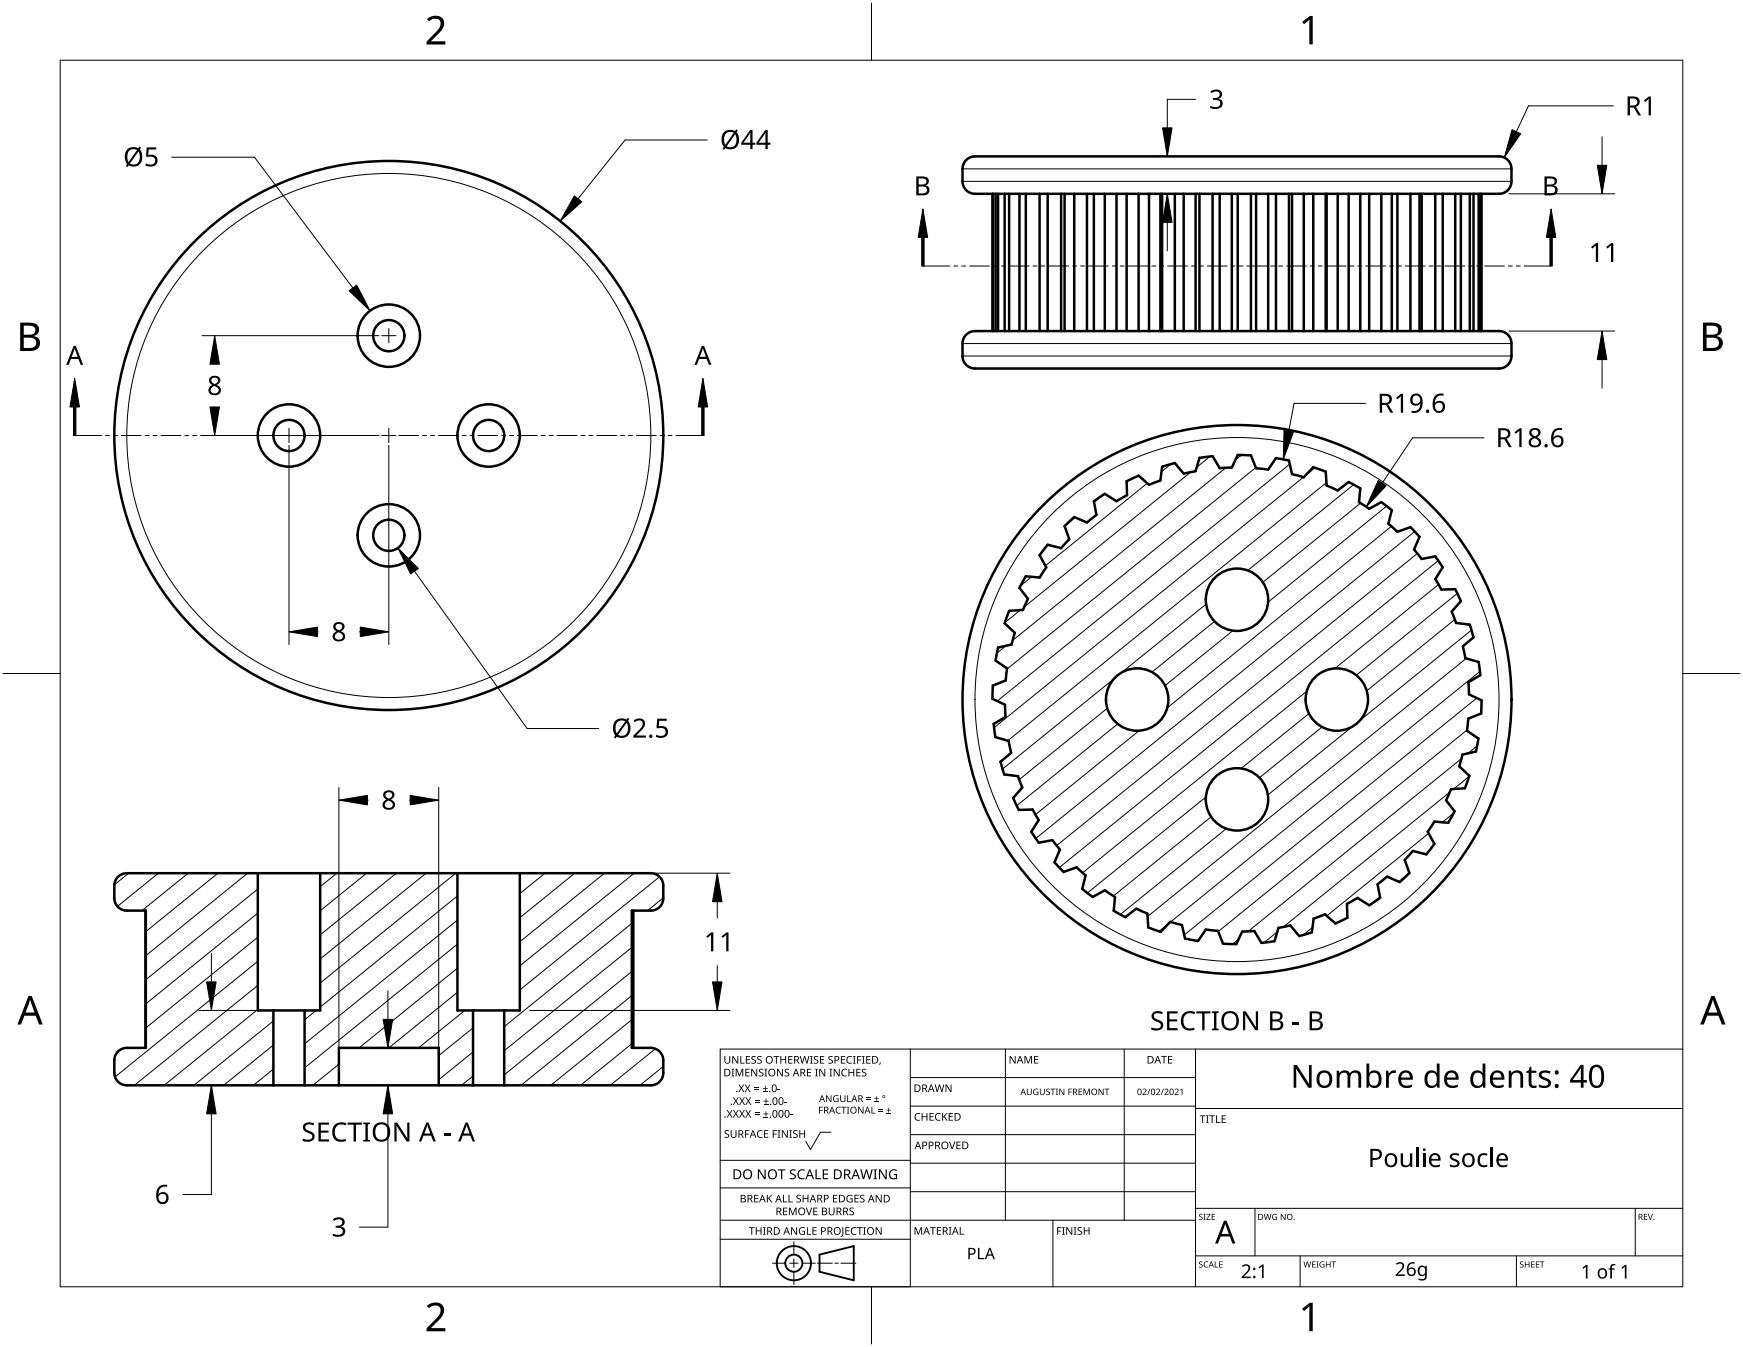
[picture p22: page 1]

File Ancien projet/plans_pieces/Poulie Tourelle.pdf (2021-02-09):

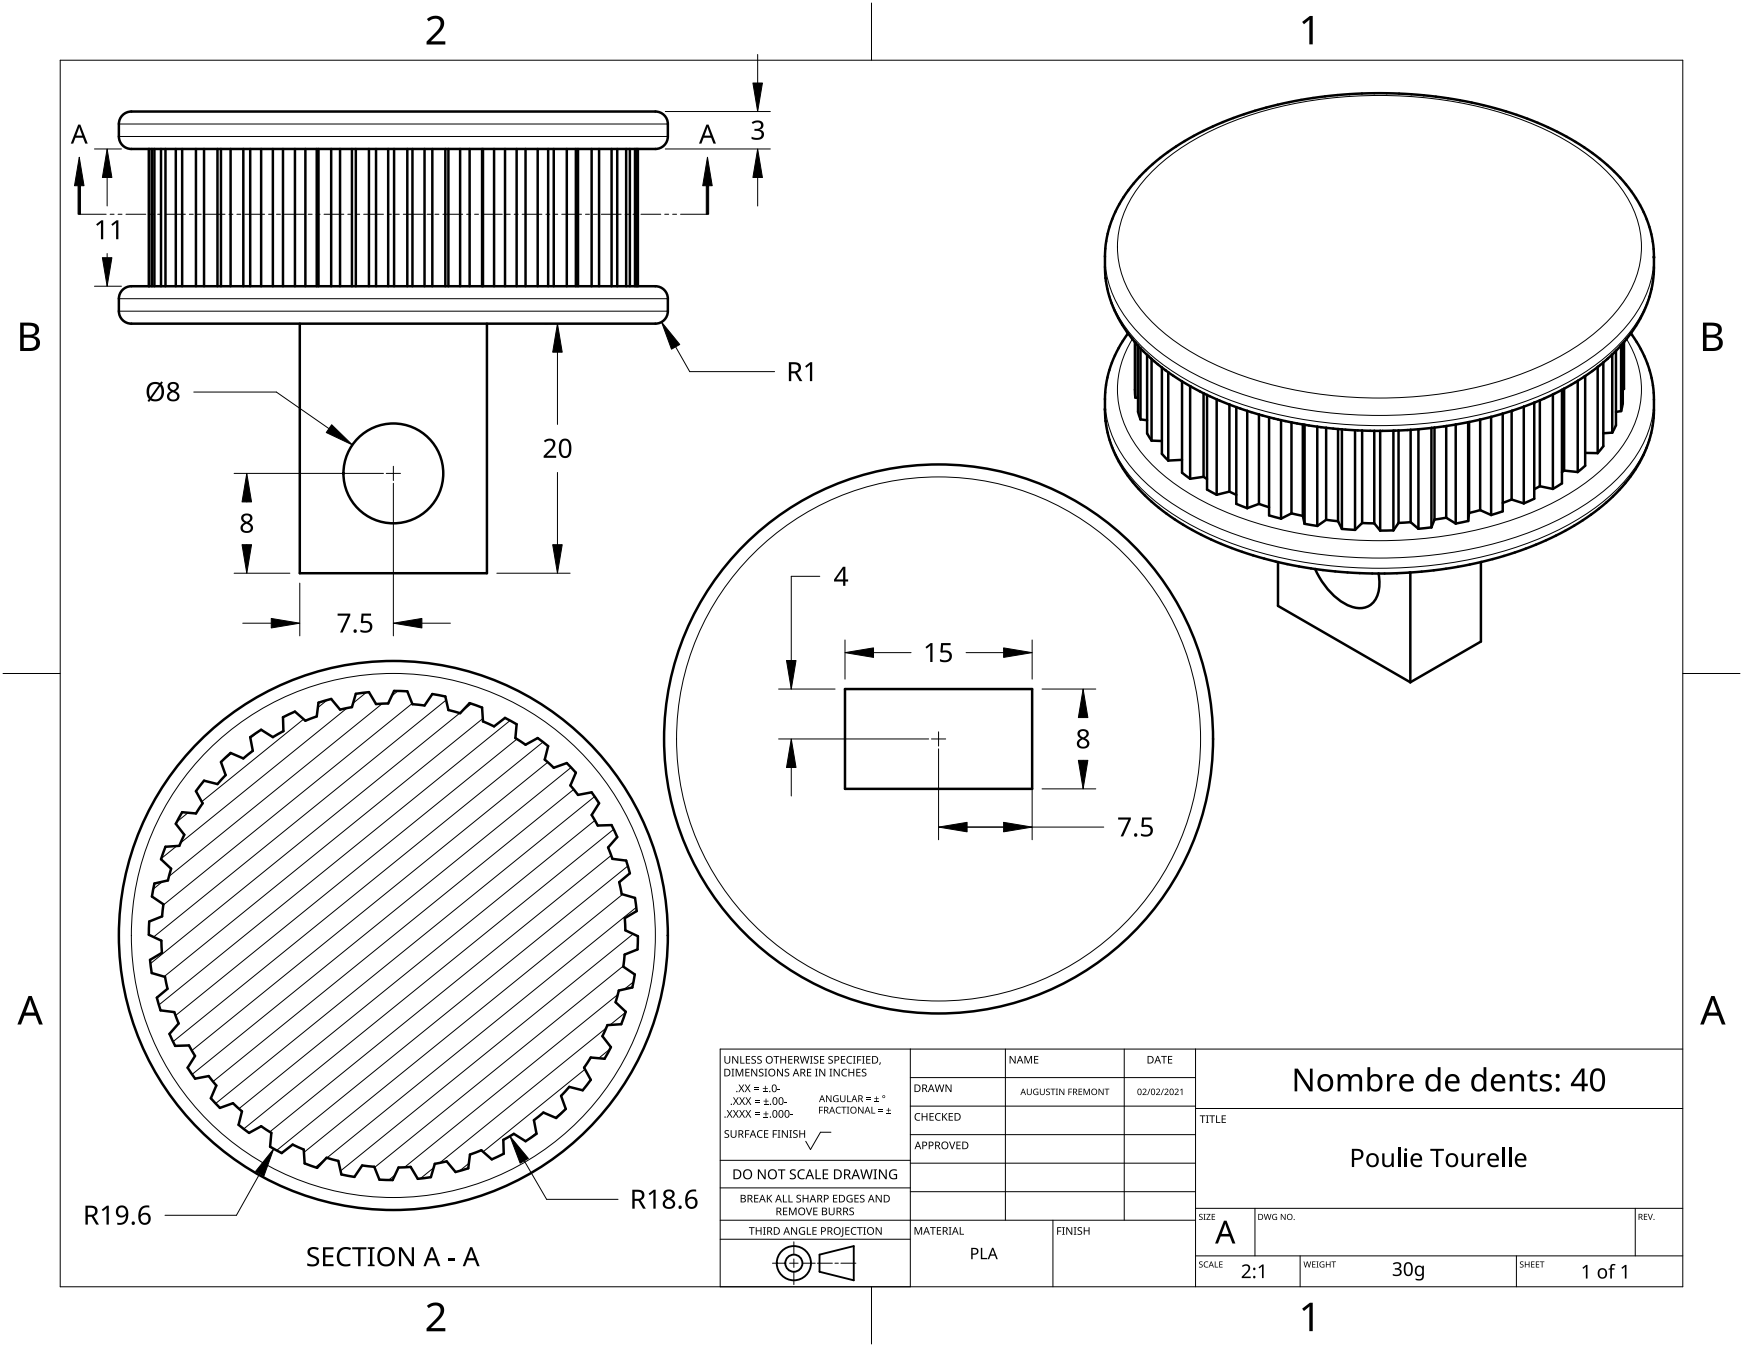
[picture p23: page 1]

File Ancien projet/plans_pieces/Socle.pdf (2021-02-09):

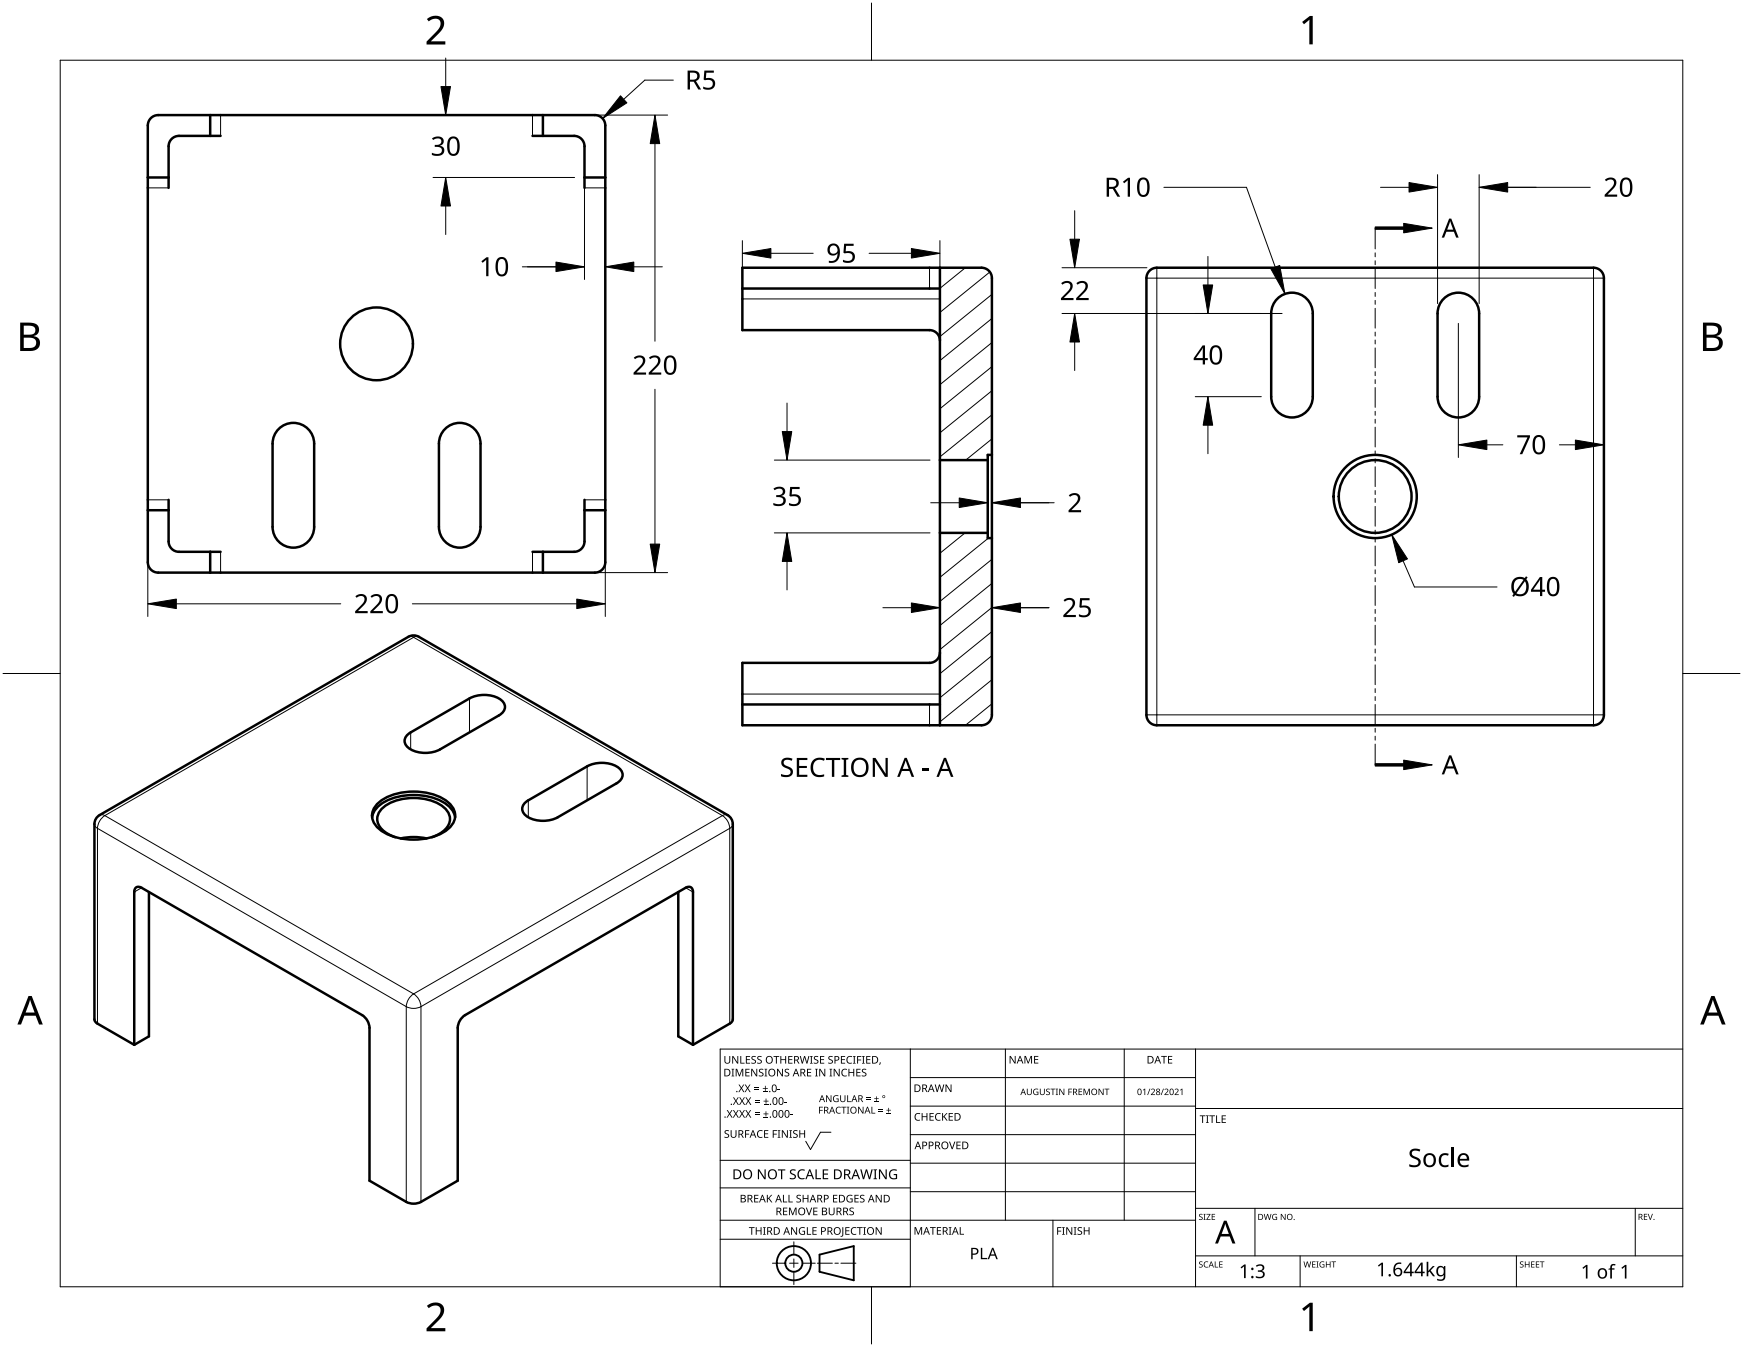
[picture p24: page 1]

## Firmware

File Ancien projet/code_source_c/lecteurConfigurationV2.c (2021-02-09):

/*******************************************************************************
* Copyright 2017 ROBOTIS CO., LTD.
*
* Licensed under the Apache License, Version 2.0 (the "License");
* you may not use this file except in compliance with the License.
* You may obtain a copy of the License at
*
*     http://www.apache.org/licenses/LICENSE-2.0
*
* Unless required by applicable law or agreed to in writing, software
* distributed under the License is distributed on an "AS IS" BASIS,
* WITHOUT WARRANTIES OR CONDITIONS OF ANY KIND, either express or implied.
* See the License for the specific language governing permissions and
* limitations under the License.
*******************************************************************************/

/* Author: Ryu Woon Jung (Leon) */

//
// *********     Sync Read and Sync Write Example      *********
//
//
// Available Dynamixel model on this example : All models using Protocol 2.0
// This example is designed for using two Dynamixel PRO 54-200, and an USB2DYNAMIXEL.
// To use another Dynamixel model, such as X series, see their details in E-Manual(emanual.robotis.com) and edit below variables yourself.
// Be sure that Dynamixel PRO properties are already set as %% ID : 1 / Baudnum : 1 (Baudrate : 57600)
//

#if defined(__linux__) || defined(__APPLE__)
#include <fcntl.h>
#include <termios.h>
#define STDIN_FILENO 0
#elif defined(_WIN32) || defined(_WIN64)
#include <conio.h>
#endif

#include <stdlib.h>
#include <stdio.h>
#include "dynamixel_sdk.h"                                  // Uses Dynamixel SDK library
#include <string.h>
#include <unistd.h>

// Control table address
#define ADDR_PRO_TORQUE_ENABLE          64                  // Control table address is different in Dynamixel model
#define ADDR_PRO_PRESENT_POSITION       132

// Data Byte Length
#define LEN_PRO_PRESENT_POSITION        4

// Protocol version
#define PROTOCOL_VERSION                2.0                 // See which protocol version is used in the Dynamixel

// Default setting
#define DXL1_ID                         1                   // Dynamixel#1 moteur de la Tourelle
#define DXL2_ID                         2                   // Dynamixel#2 moteur 1 du Bras
#define DXL3_ID                         3                   // Dynamixel#3 moteur 2 du Bras
#define DXL4_ID                         4                   // Dynamixel#4 moteur de l'Avant-Bras
#define DXL5_ID                         5                   // Dynamixel#5 moteur de la Pince

#define BAUDRATE                        115200
#define DEVICENAME                      "/dev/ttyUSB0"      // Check which port is being used on your controller
                                                            // ex) Windows: "COM1"   Linux: "/dev/ttyUSB0" Mac: "/dev/tty.usbserial-*"

#define TORQUE_ENABLE                   1                   // Value for enabling the torque
#define TORQUE_DISABLE                  0                   // Value for disabling the torque
#define DXL_MINIMUM_POSITION_VALUE      1000             // Dynamixel will rotate between this value
#define DXL_MAXIMUM_POSITION_VALUE      2040             // and this value (note that the Dynamixel would not move when the position value is out of movable range. Check e-manual about the range of the Dynamixel you use.)
#define DXL_MOVING_STATUS_THRESHOLD     20                  // Dynamixel moving status threshold

#define ESC_ASCII_VALUE                 0x1b

int getch()
{
#if defined(__linux__) || defined(__APPLE__)
  struct termios oldt, newt;
  int ch;
  tcgetattr(STDIN_FILENO, &oldt);
  newt = oldt;
  newt.c_lflag &= ~(ICANON | ECHO);
  tcsetattr(STDIN_FILENO, TCSANOW, &newt);
  ch = getchar();
  tcsetattr(STDIN_FILENO, TCSANOW, &oldt);
  return ch;
#elif defined(_WIN32) || defined(_WIN64)
  return _getch();
#endif
}

int kbhit(void)
{
#if defined(__linux__) || defined(__APPLE__)
  struct termios oldt, newt;
  int ch;
  int oldf;

  tcgetattr(STDIN_FILENO, &oldt);
  newt = oldt;
  newt.c_lflag &= ~(ICANON | ECHO);
  tcsetattr(STDIN_FILENO, TCSANOW, &newt);
  oldf = fcntl(STDIN_FILENO, F_GETFL, 0);
  fcntl(STDIN_FILENO, F_SETFL, oldf | O_NONBLOCK);

  ch = getchar();

  tcsetattr(STDIN_FILENO, TCSANOW, &oldt);
  fcntl(STDIN_FILENO, F_SETFL, oldf);

  if (ch != EOF)
  {
    ungetc(ch, stdin);
    return 1;
  }

  return 0;
#elif defined(_WIN32) || defined(_WIN64)
  return _kbhit();
#endif
}

int main()
{
  // Initialize PortHandler Structs
  // Set the port path
  // Get methods and members of PortHandlerLinux or PortHandlerWindows
  int port_num = portHandler(DEVICENAME);

  // Initialize PacketHandler Structs
  packetHandler();


  // Initialize Groupsyncread Structs for Present Position
  int groupread_num = groupSyncRead(port_num, PROTOCOL_VERSION, ADDR_PRO_PRESENT_POSITION, LEN_PRO_PRESENT_POSITION);

  
  int dxl_comm_result = COMM_TX_FAIL;               // Communication result
  uint8_t dxl_addparam_result = False;              // AddParam result
  uint8_t dxl_getdata_result = False;               // GetParam result
  

  //uint8_t dxl_error = 0;                            // Dynamixel error
  int32_t dxl1_present_position = 0, dxl2_present_position  = 0, dxl3_present_position = 0, dxl4_present_position = 0, dxl5_present_position = 0;                           // Present position


  FILE* fichier = NULL;           // Ecriture d'un fichier csv
  
  
  // Open port
  if (openPort(port_num))
  {
    printf("Succeeded to open the port!\n");
  }
  else
  {
    printf("Failed to open the port!\n");
    printf("Press any key to terminate...\n");
    getch();
    return 0;
  }

  // Set port baudrate
  if (setBaudRate(port_num, BAUDRATE))
  {
    printf("Succeeded to change the baudrate!\n");
  }
  else
  {
    printf("Failed to change the baudrate!\n");
    printf("Press any key to terminate...\n");
    getch();
    return 0;
  }
 
  
  
  // Add parameter storage for Dynamixel#1 present position value
  dxl_addparam_result = groupSyncReadAddParam(groupread_num, DXL1_ID);
  if (dxl_addparam_result != True)
  {
    fprintf(stderr, "[ID:%03d] groupSyncRead addparam failed", DXL1_ID);
    return 0;
  }

  // Add parameter storage for Dynamixel#2 present position value
  dxl_addparam_result = groupSyncReadAddParam(groupread_num, DXL2_ID);
  if (dxl_addparam_result != True)
  {
    fprintf(stderr, "[ID:%03d] groupSyncRead addparam failed", DXL2_ID);
    return 0;
  }
  
  // Add parameter storage for Dynamixel#3 present position value
  dxl_addparam_result = groupSyncReadAddParam(groupread_num, DXL3_ID);
  if (dxl_addparam_result != True)
  {
    fprintf(stderr, "[ID:%03d] groupSyncRead addparam failed", DXL3_ID);
    return 0;
  }
  
  // Add parameter storage for Dynamixel#4 present position value
  dxl_addparam_result = groupSyncReadAddParam(groupread_num, DXL4_ID);
  if (dxl_addparam_result != True)
  {
    fprintf(stderr, "[ID:%03d] groupSyncRead addparam failed", DXL4_ID);
    return 0;
  }
  
  // Add parameter storage for Dynamixel#5 present position value
  dxl_addparam_result = groupSyncReadAddParam(groupread_num, DXL5_ID);
  if (dxl_addparam_result != True)
  {
    fprintf(stderr, "[ID:%03d] groupSyncRead addparam failed", DXL5_ID);
    return 0;
  }
  
  
  
  
  while (1)
  {
    
    
    printf("Pour enregistrer la traj de montée appuie sur espace (or press ESC to quit!)\n");    
    
    if (getch() == ESC_ASCII_VALUE)
      break;

    fichier = fopen("Configuration1.csv" , "w");

    double Fe = 20;
    double Te = 10;
    int i = 0;
    
    while (i< Te*Fe)
    
    {
    
    // Syncread present position
    groupSyncReadTxRxPacket(groupread_num);
    if ((dxl_comm_result = getLastTxRxResult(port_num, PROTOCOL_VERSION)) != COMM_SUCCESS)
      printf("%s\n", getTxRxResult(PROTOCOL_VERSION, dxl_comm_result));

    // Check if groupsyncread data of Dynamixel#1 is available
    dxl_getdata_result = groupSyncReadIsAvailable(groupread_num, DXL1_ID, ADDR_PRO_PRESENT_POSITION, LEN_PRO_PRESENT_POSITION);
    if (dxl_getdata_result != True)
    {
      fprintf(stderr, "[ID:%03d] groupSyncRead getdata failed", DXL1_ID);
      return 0;
    }

    // Check if groupsyncread data of Dynamixel#2 is available
    dxl_getdata_result = groupSyncReadIsAvailable(groupread_num, DXL2_ID, ADDR_PRO_PRESENT_POSITION, LEN_PRO_PRESENT_POSITION);
    if (dxl_getdata_result != True)
    {
      fprintf(stderr, "[ID:%03d] groupSyncRead getdata failed", DXL2_ID);
      return 0;
    }
    
    // Check if groupsyncread data of Dynamixel#3 is available
    dxl_getdata_result = groupSyncReadIsAvailable(groupread_num, DXL3_ID, ADDR_PRO_PRESENT_POSITION, LEN_PRO_PRESENT_POSITION);
    if (dxl_getdata_result != True)
    {
      fprintf(stderr, "[ID:%03d] groupSyncRead getdata failed", DXL3_ID);
      return 0;
    }
    
    // Check if groupsyncread data of Dynamixel#4 is available
    dxl_getdata_result = groupSyncReadIsAvailable(groupread_num, DXL4_ID, ADDR_PRO_PRESENT_POSITION, LEN_PRO_PRESENT_POSITION);
    if (dxl_getdata_result != True)
    {
      fprintf(stderr, "[ID:%03d] groupSyncRead getdata failed", DXL4_ID);
      return 0;
    }

    // Check if groupsyncread data of Dynamixel#5 is available
    dxl_getdata_result = groupSyncReadIsAvailable(groupread_num, DXL5_ID, ADDR_PRO_PRESENT_POSITION, LEN_PRO_PRESENT_POSITION);
    if (dxl_getdata_result != True)
    {
      fprintf(stderr, "[ID:%03d] groupSyncRead getdata failed", DXL5_ID);
      return 0;
    }



    // Get Dynamixel#1 present position value
    dxl1_present_position = groupSyncReadGetData(groupread_num, DXL1_ID, ADDR_PRO_PRESENT_POSITION, LEN_PRO_PRESENT_POSITION);
    
    // Get Dynamixel#2 present position value
    dxl2_present_position = groupSyncReadGetData(groupread_num, DXL2_ID, ADDR_PRO_PRESENT_POSITION, LEN_PRO_PRESENT_POSITION);
    
    // Get Dynamixel#3 present position value
    dxl3_present_position = groupSyncReadGetData(groupread_num, DXL3_ID, ADDR_PRO_PRESENT_POSITION, LEN_PRO_PRESENT_POSITION);
    
    // Get Dynamixel#4 present position value
    dxl4_present_position = groupSyncReadGetData(groupread_num, DXL4_ID, ADDR_PRO_PRESENT_POSITION, LEN_PRO_PRESENT_POSITION);
    
    // Get Dynamixel#5 present position value
    dxl5_present_position = groupSyncReadGetData(groupread_num, DXL5_ID, ADDR_PRO_PRESENT_POSITION, LEN_PRO_PRESENT_POSITION);

   
    float temps = i*1/Fe;
    
    if (fichier != NULL)
    {
 	
 			
    	fprintf(fichier, "%f,%03d,%03d,%03d,%03d,%03d\n", temps, dxl1_present_position, dxl2_present_position, dxl3_present_position, dxl4_present_position, dxl5_present_position);
		
       
     }
 	
	
  usleep(1/Fe*1e6);
  i++;
  }
  fclose(fichier);


    
    printf("Enregistre la descente ! (or press ESC to quit!)\n");
    
    if (getch() == ESC_ASCII_VALUE)
      break;

    fichier = fopen("Configuration2.csv" , "w");
    i = 0;
    
    while (i< Te*Fe)
    
    {
    
    // Syncread present position
    groupSyncReadTxRxPacket(groupread_num);
    if ((dxl_comm_result = getLastTxRxResult(port_num, PROTOCOL_VERSION)) != COMM_SUCCESS)
      printf("%s\n", getTxRxResult(PROTOCOL_VERSION, dxl_comm_result));

    // Check if groupsyncread data of Dynamixel#1 is available
    dxl_getdata_result = groupSyncReadIsAvailable(groupread_num, DXL1_ID, ADDR_PRO_PRESENT_POSITION, LEN_PRO_PRESENT_POSITION);
    if (dxl_getdata_result != True)
    {
      fprintf(stderr, "[ID:%03d] groupSyncRead getdata failed", DXL1_ID);
      return 0;
    }
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

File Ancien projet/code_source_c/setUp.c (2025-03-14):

//CODE LED RGB (https://www.admfactory.com/blinking-led-on-raspberry-pi-using-c/)

#include <wiringPi.h>
#include <wiringPiI2C.h>
#include <stdlib.h>
#include <stdio.h>

// Define some device parameters
#define I2C_ADDR   0x27 // I2C device address

#define LedGreenPin 0
#define LedBluePin 2
#define LedRedPin 3
#define sensorPin 4

// Define some device constants
#define LCD_CHR  1 // Mode - Sending data
#define LCD_CMD  0 // Mode - Sending command

#define LINE1  0x80 // 1st line
#define LINE2  0xC0 // 2nd line

#define LCD_BACKLIGHT   0x08  // On
// LCD_BACKLIGHT = 0x00  # Off

#define ENABLE  0b00000100 // Enable bit

// fonction ecran lcd
void lcd_init(void);
void lcd_byte(int bits, int mode);
void lcd_toggle_enable(int bits);
void lcdLoc(int line); //move cursor
void ClrLcd(void); // clr LCD return home
void typeln(const char *s);
int fd;

//Fonctions des messages IronFork
void messageSalut(void){
    
    
    ClrLcd();
    lcdLoc(LINE1);
    typeln("Salut! Je suis");
    lcdLoc(LINE2);
    typeln("   IronFork");
    delay(3000);

    ClrLcd();
    lcdLoc(LINE1);
    typeln("Allons manger!");
    delay(3000);
}

void messageApprendreTraj(void){
    
    ClrLcd();
    lcdLoc(LINE1);
    typeln("Voulez-vous");
    delay(2000);

    ClrLcd();
    lcdLoc(LINE1);
    typeln("apprendre une");
    lcdLoc(LINE2);
    typeln("trajectoire ?");
    delay(2000);

}

void messageRecuperationTraj(void){
    
    ClrLcd();
    lcdLoc(LINE1);
    typeln("Recuperation de");
    lcdLoc(LINE2);
    typeln("la trajectoire");
    delay(2000);
    

}

void messageTrajCharge(void){
    
    ClrLcd();
    lcdLoc(LINE1);
    typeln("Trajectoire");
    lcdLoc(LINE2);
    typeln("chargee !");
    delay(2000);
    

}

void messageNouvelleTraj(void){
    ClrLcd();
    lcdLoc(LINE1);
    typeln("Nouvelle");
    lcdLoc(LINE2);
    typeln("trajectoire !");
    delay(2000);

}

void messageLancementCycle(void){
    
    ClrLcd();
    lcdLoc(LINE1);
    typeln("Pour manger ...");
    delay(2000);

    
    
    ClrLcd();
    lcdLoc(LINE1);
    typeln("appuie sur");
    lcdLoc(LINE2);
    typeln("le bouton !!");
 
 

}

void messageCycle(void){
    ClrLcd();
    lcdLoc(LINE1);
    typeln("Cycle en");
    lcdLoc(LINE2);
    typeln("cours !!");
    

}

//FONCTIONS POUR ALLUMER ET ETEINDRE LES LEDS

void turnOnLedGreen(void){
	digitalWrite(LedGreenPin, HIGH);   //led on
}
void turnOnLedBlue(void){
	digitalWrite(LedBluePin, HIGH);   //led on
}
void turnOnLedRed(void){
	digitalWrite(LedRedPin, HIGH);   //led on
}

void turnOffLedGreen(void){
	digitalWrite(LedGreenPin, LOW);   //led off
}
void turnOffLedBlue(void){
	digitalWrite(LedBluePin, LOW);   //led off
}
void turnOffLedRed(void){
	digitalWrite(LedRedPin, LOW);   //led off
}
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

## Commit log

2021-01-13 path files code
    [PELLETAGEV4.xlsx]
2021-02-01 Create Assemblages
